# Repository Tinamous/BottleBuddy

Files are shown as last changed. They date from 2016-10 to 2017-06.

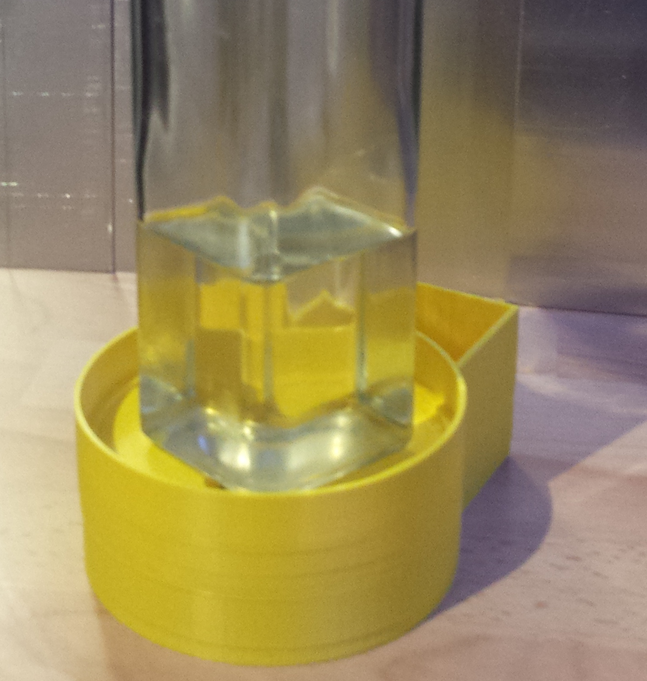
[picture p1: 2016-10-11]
Media/SmallOliveOil.png

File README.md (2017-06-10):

# BottleBuddy

Bottle Buddy is a Internet connected smart scale to monitor the amount of product in a bottle.

## Uses

* Stock control of bottled products
** Chemicals in a lab
** Reagents at a testing station
** Shampoo in a salon
** Domestic products (bleach, shampoo, etc) in the home.
** Liquors/spirits in a bar
* Monitoring chemicals in a lab to track usage (e.g. poisons usage)
* Refilling of reagents bottles
* Supply management to facilitate re-ordering as the bottle gets empty or used.
* Predictive ordering based on use
* Shelf life tracking from initial receipt and first use

### Example use case:

A river polution testing laboratory uses pH 4 and 7 buffer solutions to calibrate their pH Electrodes. 
Tests are run most days the electrodes are calibrated at least once, they use approximatly 25-75ml from each buffer solution.
The buffer solution which comes in 1L bottles with each bottle costs $70.
Once the buffer is opened it needs to be used within 28 days and has a shelf life of 1 year from the date of delivery.

Due to the cost and shelf life the lab only orders a new bottle of each buffer solution when they are getting low allowing for about a 3 day delivery time.

The lab is a remote testing station which is only occupied whilst the technician is there for a few hours running the tests, the technician is responsible 
for brining the required reagents with them as and when new stock is needed.

#### How Bottle Buddy helps

Delivery of new Reagents:

When new buffer solutions are brought a RFID sticked is placed on the bottom of the bottle to track it. The bottle is then placed on the Bottle Buddy where it
registers the RFID identifier and an initial weight, this is logged and as the RFID token is new the bottle assigned a delivery date to ensure that the 
shelf life restriction is monitored. 

By knowing the location of the Bottle Buddy the system also knows the location of this reagent, the technician can then use their phone or computer to 
assign additional details to the bottle as required and possibly print out a more human readable label to go with the bottle. This additional data may have been pre-programmed 
into the FRID tags (e.g. they may have tags specifically for the pH 7 buffer which include meta-data about shelf life, reagent name, etc.), or they may use a 
special identity tag after the reagent has been placed on Bottle Buddy to indicate it's type.

Day to day usage:

Once the technician has finished for the day they clean up and put away the equipment, part of this includes dropping each of the buffer
solution bottles onto Bottle Buddy, which then measures the weight of the bottle and records this. When the bottle weight drops below a 
pre-defined level, or the system determins the bottle will be empty within a certain timeframe an email is sent to the purchasing 
department or stores requesting a new bottle be delivered to the technician.

By tracking the weight of the bottle the tracking applicaiton can tell that the reagent is in use (i.e. the weight has decreased indicating it has
been opened and is in use), this allows the tracking of the shortened shelf life to ensure that a replacement is available before the 28 day usage is up.

Emails sent to the purchasing department can include details of when this reagent is required by, how much is typically used and who needs it, order codes and other information required for purchasing.

Other than the very brief initial RFID token assignment and the few seconds required to put the reagen on Bottle Buddy at the end of the day no time is 
lost with requesting replacement reagents, or discovering that the reagent has run out because the technician forgot to re-order any, good quality
reagent can be assured by the tracking of shelf life, and improved planning by usage monitoring can be achieved.

## Features: 

### V1.0

* Weight measurement with HX711 PCB and Load Cell
* Potential to drive NeoPixel ring (needs to be run from battery as 5V USB supply will cause problems).
* WiFi connectivity with Particle Photon
* Doesn't provide much in the way of power saving options, the Photon can be put to sleep and woken to check for an item on the scale. An accelerometer
can be added by connecting the wires to the appropriate I2C and power pins and glued to the PCB.
* Simple construction, can be hand soldered.

### V1.1

* Has an accelerometer (MMA8452Q)to detect a pulse when something is placed on the scale
* Photon can be kept in deep sleep and woken by the accelerometer to enable longer battery life.
* Power to the NFC PCB and optional NeoPixels can be controlled via p-Channel MOSFET switches.
* Charge monitoring for Li-Ion batteries with a Max1704x
* Simple temperature measurements with a DS18B20 (which could be glued to the load cell for better accuracy if needed)
* Temperature, humidity and pressure measurements with a BME280
* Swapped to headerless Photon to reduce depth of PCB on both sides
* Piezo buzzer to provide user feedback
* Single point LED at the front of the top to provide simple user feedback
* Needs reflow soldering / stencil for the BME280, Max1704x and MMA8452Q - these can all be left off through for more basic functionality

## Modes of operation

## 3D Printable

Boddle Buddy is made of two main shells, a top and a bottom. Both are designed so that the user facing part should have a nice smooth finish.

### Base - BottleBuddyBase.scad/.stl

This is the lower half of the assembly, it has holes for the the counter sunk M5x16 machine screws required by the load cell, [currently] a hole for 
the HX711 load cell amplifier PCB to be mounted (this is expected to be PCB mounted from V1.1 of the PCB), and a compartment for the battery to 
sit in.

It has 4 10mm recesses for feet to be placed in so that the floor isn't resting on a possibly uneven surface.

It may also have a hole to provide power in (depending on options

### Top - BottleBuddyTop.scad/.stl

This is the upper half, the PCB is mounted to the inside of this. This is connected to the lower half only by means of the load cell.

A skirt is printed aroud below the top half to prevent ingress of liquid into the lower half from above and to improve the look (rather than having a void). The skirt has a clearance around it to 

The load cell uses 2x M4x20 counter sunk machine screws from the top.

Inset in the top is a PN532 NFC reader (e.g. http://www.ebay.co.uk/itm/NXP-PN532-NFC-RFID-Module-V3-Kits-Reader-Writer-For-Arduino-Android-Phone-Module-/291939590305?hash=item43f8f4a0a1:g:p2kAAOSwnbZYJTmy)

This requires connecting up through the I2C connection with a 4 way header (solder into the NFC module first) through to the lower PCB, as well as 2 wires from the RSTO and IRQ pads connecting to the appropriate "test points" on the PCB.

The main PCB should be fitted inside with 2x self tappers through the holes either side of the load cell. 

The open hole for the LED on the V1.1 PCB (not present on the V1.0 PCB) should be covered with electrical tape to prevent resin coming through when poured onto the top.

When everything is mounted it can be tested to check for connection problems and then a layer of clear epoxy resin poured onto the top to the level of the raised lip (or just below to prevent overflow!)

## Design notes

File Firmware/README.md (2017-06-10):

# BottleBuddy Firmware

This folder contains the firmware required to run the BottleBuddy as a Reagent Tracker. 

This is based on the Particle Photon. It is assumed you are familiar with programming the Photon via the Particle Build system.

## Programming the Photon

To use the code open a new code application in the Particle Build environment (https://build.particle.io)

Unfortunatly at present Particle don't have a nice way to bundle applications for sharing using the build environment, you can use their console based compiler if you prefer, but this guide is for the web ide.

Create a new Application (<>).

Paste in the bottlebuddy-v1.0.ino code.

Add the following libraries using the Build library manager:

* Adafruit_PN532
* neopixel
* OneWire

Add new tabs using the (+) in the top right:

* HX711
* SparkFunMMQ8452Q

You should get a .cpp and .h tab for each of those. Paste in the appropriate files (note theirs a bit of a bug where pasting in the .cpp code will end up in the .h file as well).

The HX711 library is available through the Particle Library system as HX711ADC however I had some issues with it at the original time of writing so brought it into the project as a C++ file, also the tare function uses an incorrect type (double should be long). 

The MMQ8452Q library didn't support configuration of tap interrupt events so I've modified that slightly from the original SparkFun library to support Tap Interrupts.

You will find the build environment has duplicated the #include statements. Remove the duplicates.

Ensure that the pin definitions in the .ino file match your build, these have changed between V1.0 and V1.1 of the PCB.

Click the verify icon and the application should build.

Ensure you have the correct device selected and the firmware version is set to 6.2 then flash the photon code.

## Post Programming:

Once the Photon has flashed it is going to spend most of its time asleep so we won't be able to re-flash the device without doing something special. 

Their are a few ways to keep the Photon connected to allow firmware updates. The KeepAwake pin (A2) is probably the most useful, particularly on a prototype board set-up. V1.1 of the PCB has a test point that can be soldered too if required.

Alternatively we can place the Photon in Safe Mode. 

To place the photon in Safe Mode, hold both Set-Up and Reset buttons down, release Reset and wait for the LED to flash Purple (it does this almost immediately), then release the Set-Up button. The Photon will now connect to the Particle Cloud and we can updated it, but it won't run any of our code until it is reset (manual or due to firmware update).

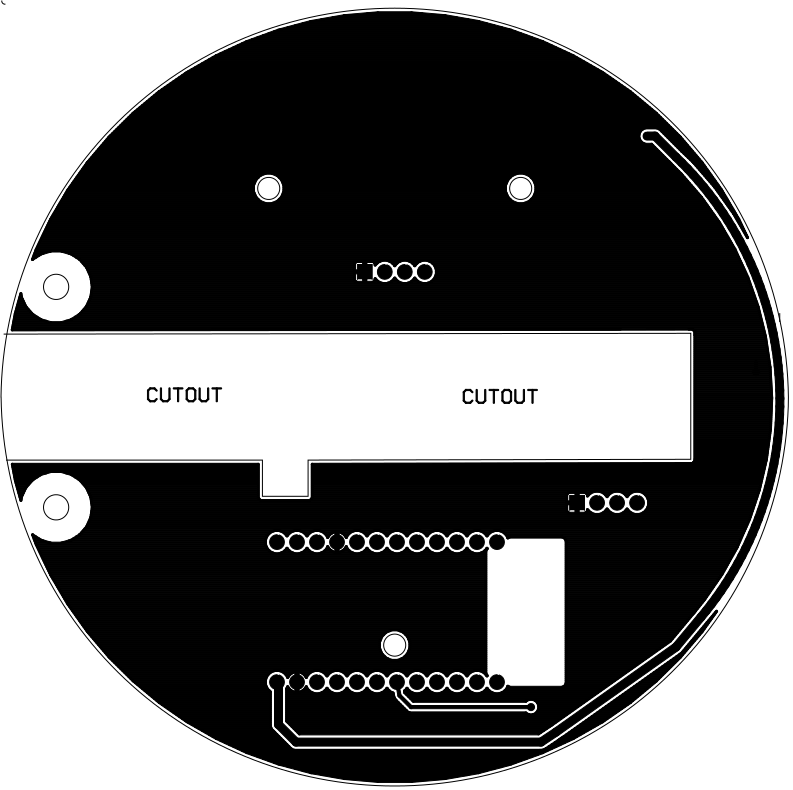
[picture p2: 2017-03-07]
Media/PCB/bottom_copper.png

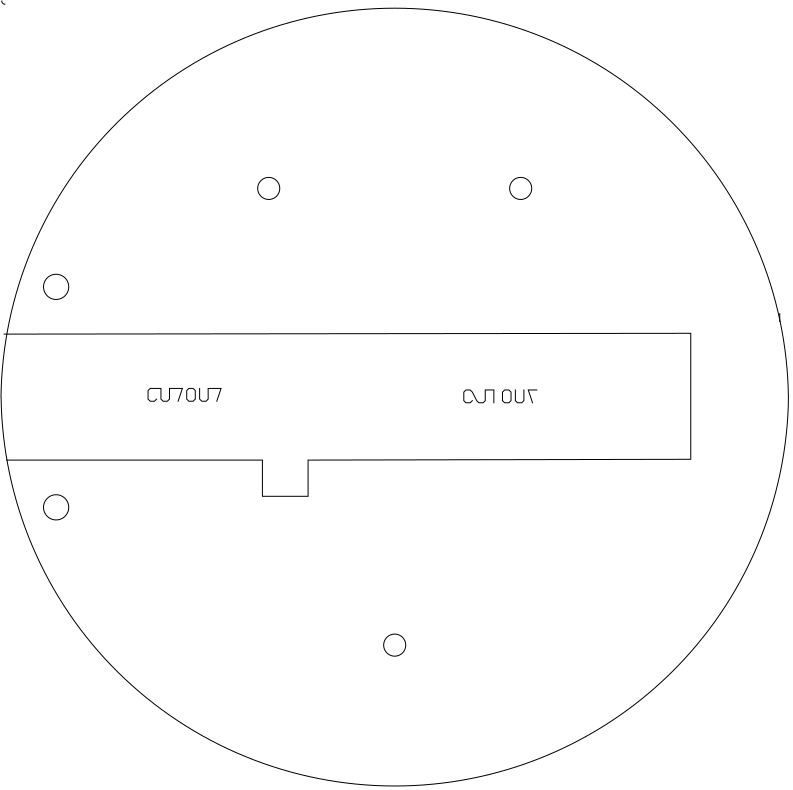
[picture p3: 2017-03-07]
Media/PCB/mill.png

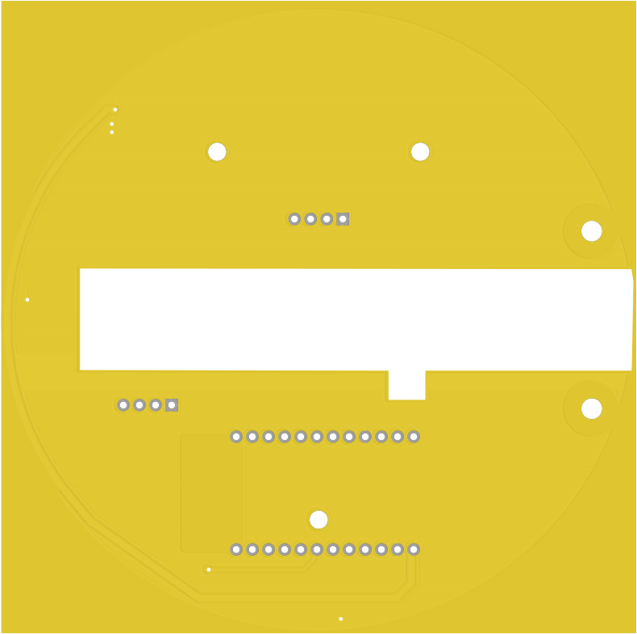
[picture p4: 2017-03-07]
Media/PCB/bottom.png

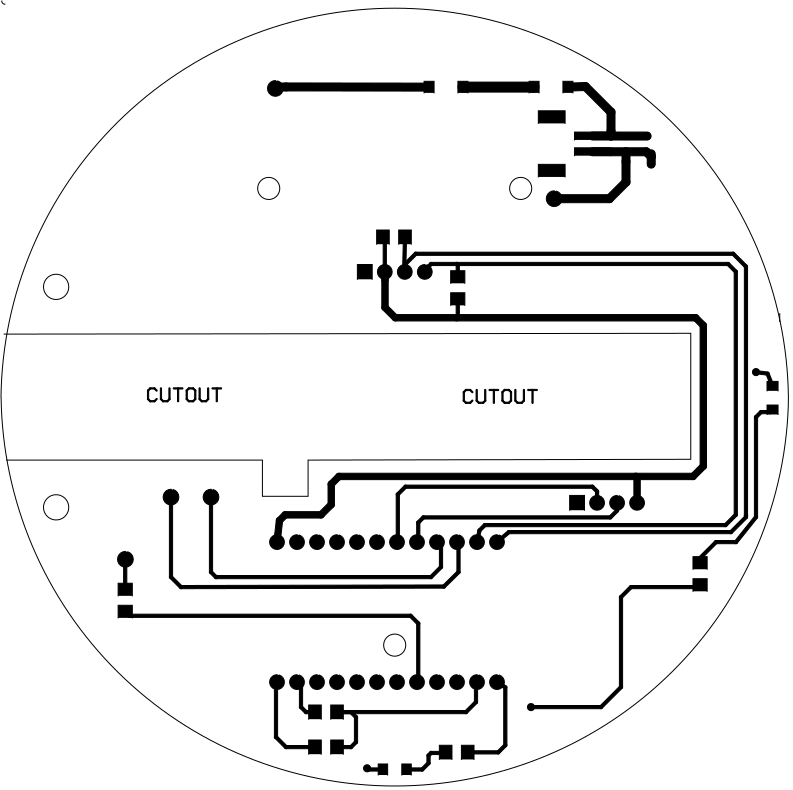
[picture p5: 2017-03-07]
Media/PCB/top_copper.png

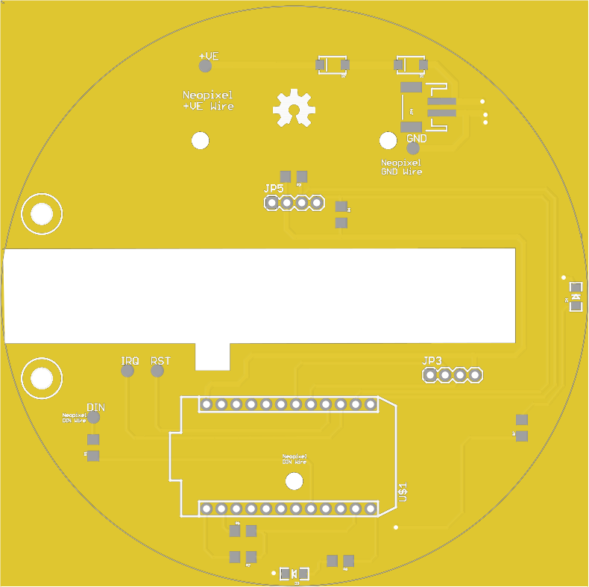
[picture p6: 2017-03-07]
Media/PCB/top.png

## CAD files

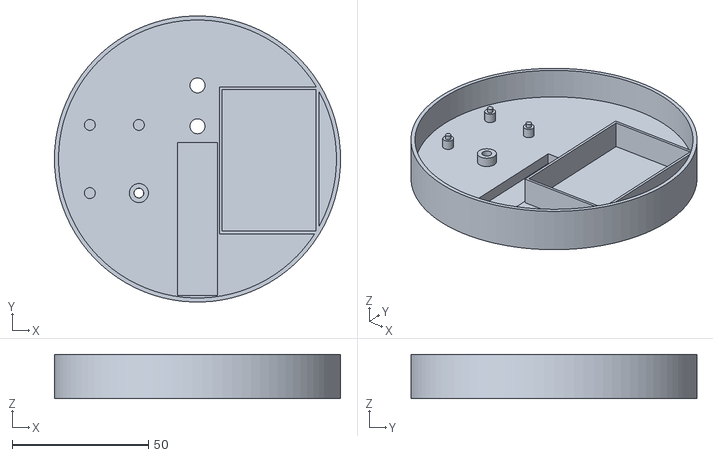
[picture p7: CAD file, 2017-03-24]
BottleBuddyBase.stl
105.0 x 104.9 x 16.2

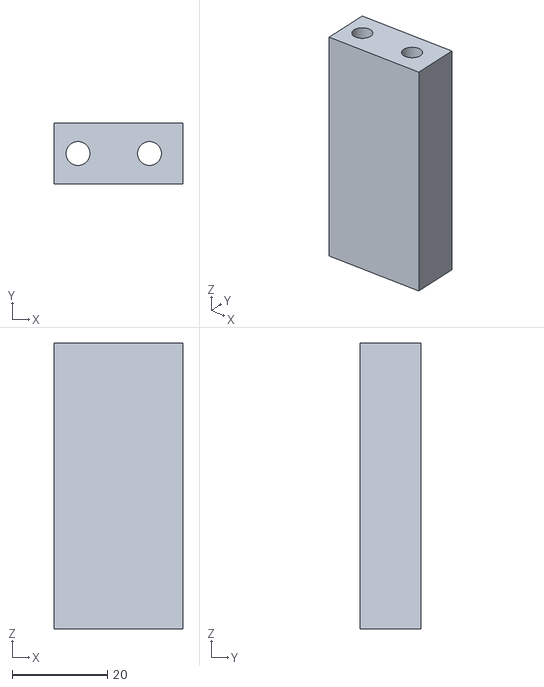
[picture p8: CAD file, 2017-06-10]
Case/ExtraBits/LoadCellSpacer-60mm.stl
27.0 x 12.8 x 60.0

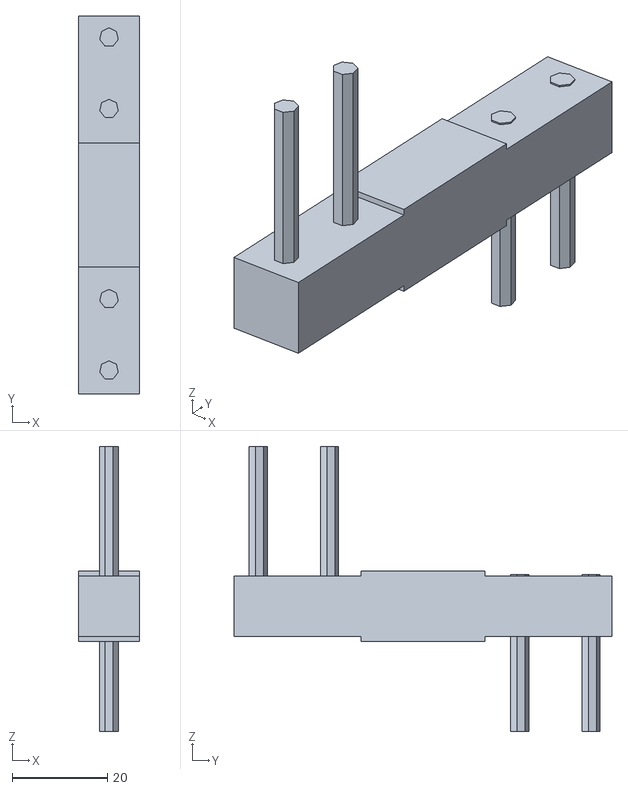
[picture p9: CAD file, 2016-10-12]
Case/LoadCellModel.stl
12.8 x 79.5 x 60.0

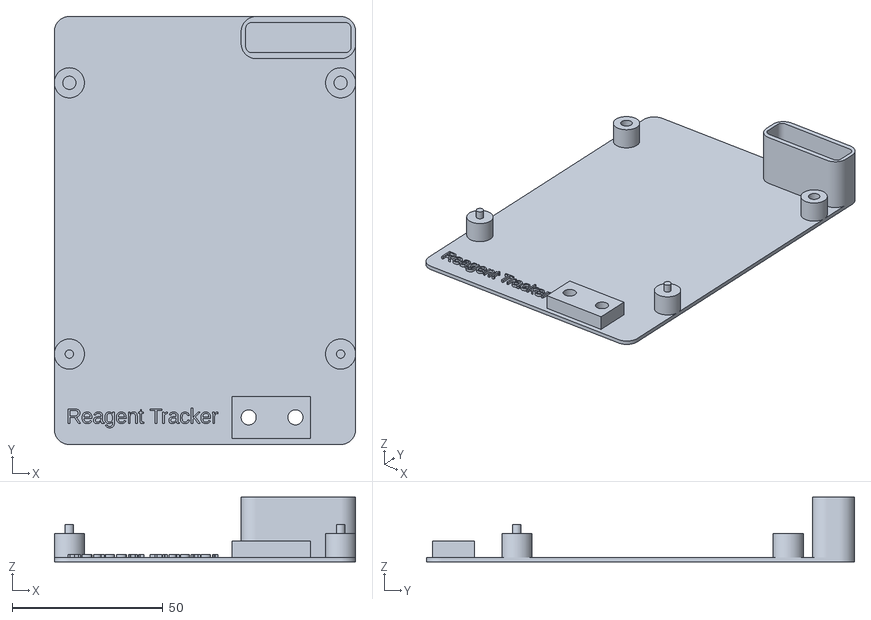
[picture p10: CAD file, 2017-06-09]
Case/Prototype/PrototypeBaseWithLoadCell.stl
100.0 x 142.0 x 21.5

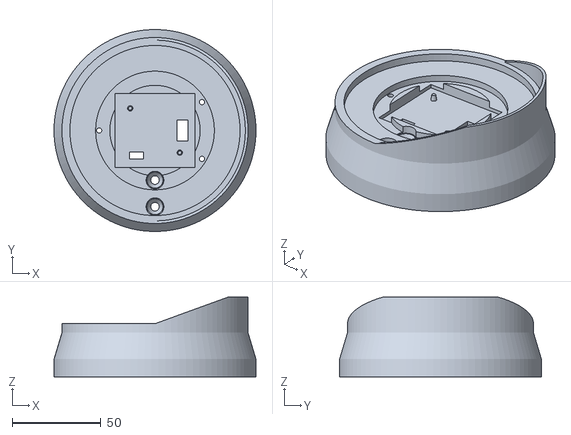
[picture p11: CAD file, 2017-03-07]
BottleBuddyTop.stl
114.0 x 113.9 x 45.0

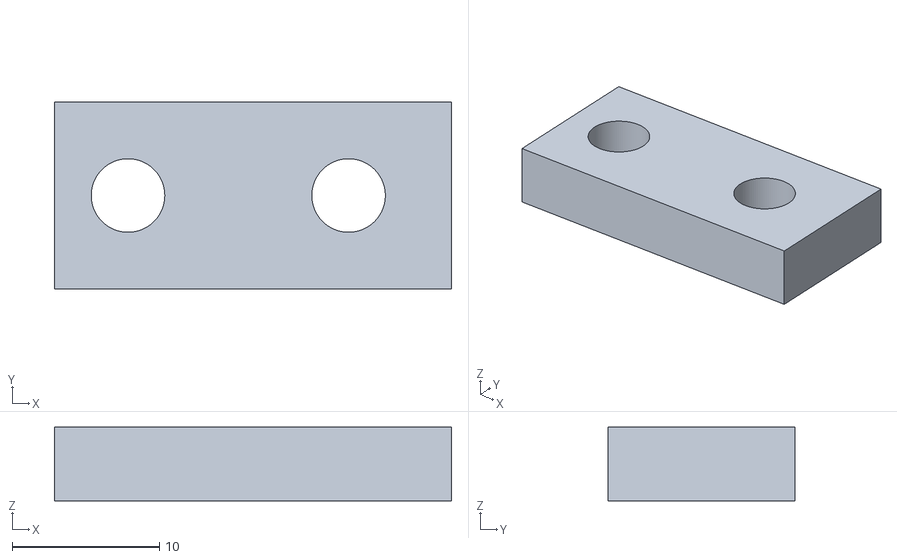
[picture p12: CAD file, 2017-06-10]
Case/ExtraBits/LoadCellSpacer-5mm.stl
27.0 x 12.8 x 5.00

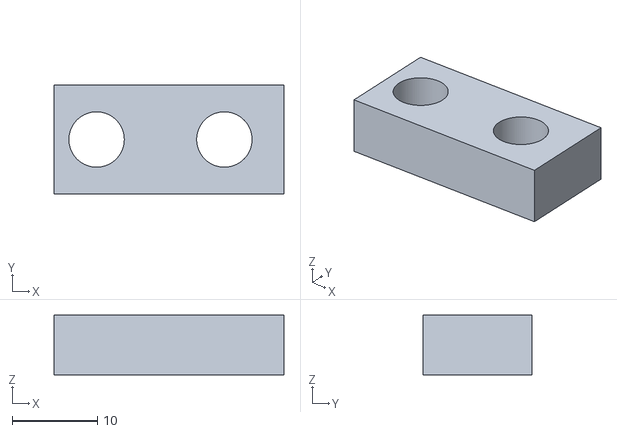
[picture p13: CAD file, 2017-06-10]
Case/ExtraBits/LoadCellSpacer-7mm.stl
27.0 x 12.8 x 7.00

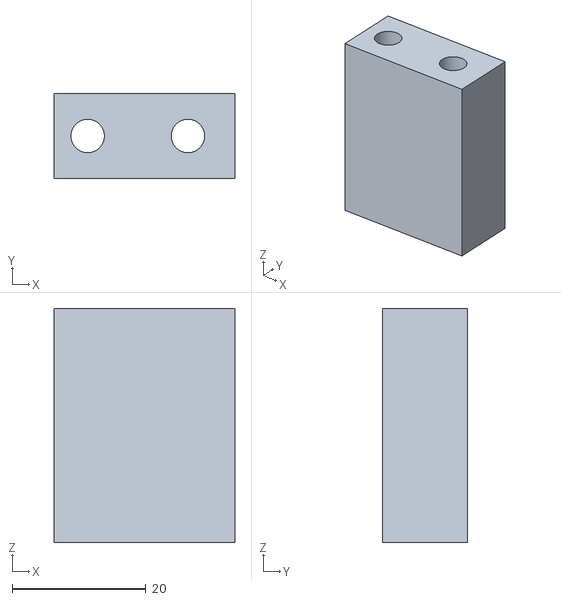
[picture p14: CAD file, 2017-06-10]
Case/ExtraBits/LoadCellSpacer-35mm.stl
27.0 x 12.8 x 35.0

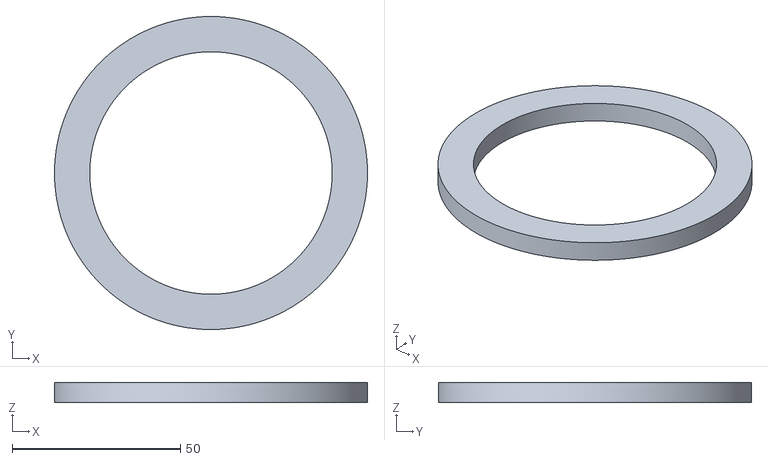
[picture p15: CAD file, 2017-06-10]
Case/ExtraBits/TopSpacer.stl
93.0 x 93.0 x 6.00

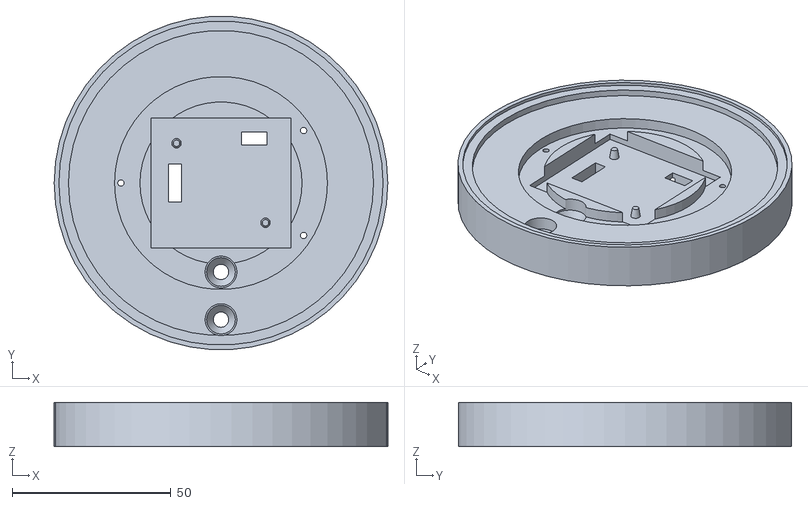
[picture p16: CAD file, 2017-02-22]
Case/ExtraBits/NfcAndNeoPixelCutouts.stl
105.0 x 104.8 x 14.0

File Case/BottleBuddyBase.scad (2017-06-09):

$fn = 360;
bottleDiameter = 100;
wallThickness = 3;
bottlePadding = 2;
baseFloorThickness = 2;

loadcellHeight = 12.75;
loadcellWidth = 12.75;
loadcellLength = 79.5;
loadCellOffset = -48;

gabBetweenTopAndBottom = 1.5;
wallHeight=baseFloorThickness + loadcellHeight - gabBetweenTopAndBottom;

// Dont need such a large height as the top covers most of it.
wallHeight = 5;
echo ("WallHeight (i.e. total height)=" ,wallHeight);

loadCellPcbXOffset = -36;
loadCellPcbYOffset = -32;
loadCellPcbWidth = 21;
loadCellPcbSpaceBetweenHoles = 18;

// ====================================================
// Models
// ====================================================
module showBottleHolder() {
    import("BottleBuddyTop.stl");
}

module QIReceiver() {
    color("Black", 50) {
        cube([45, 75,1]);
    }
}

module loadCellPcb() {
    cube([23, 33, 6]);
    
    translate([2.5,2.5, -3]) {
        cylinder(d=2, h=20);
        
        translate([0,25, 0]) {
            cylinder(d=2, h=20);
        }
    }
    
    // 15mm gap between screws
    
    translate([2.5 + loadCellPcbSpaceBetweenHoles,2.5, -3]) {
        cylinder(d=2, h=20);
        
        translate([0,25, 0]) {
            cylinder(d=2, h=20);
        }
    }
}

module importLoadCellModel() {
    import("LoadCellModel.stl");
}

// Load cell model to project into the design for fit.
module loadCell() {
    //import("LoadCellModel.stl");
    
    //translate([-30,-(loadcellWidth/2),-2]) {
    rotate([0,0,90]) {
        translate([loadCellOffset, -(loadcellWidth)/2 ,-0.1]) {
        
        //color("Gainsboro", 50) { 
            difference() {
                union() {
                    cube([loadcellLength, loadcellWidth, loadcellHeight]);
                    // strain gauge placement + goo
                    translate([(loadcellLength-26)/2,0,loadcellHeight]) {
                        cube([26,loadcellWidth,1]);
                    }
                    translate([(loadcellLength-26)/2,0,-1]) {
                        cube([26,loadcellWidth,1]);
                    }
                }
                union() {
                    translate([5.0, (12.75/2),0]) {
                        // Bigger top connector holes
                        // to help align with top when visual testing
                        #cylinder(d=4, h=40);
                    }
                    translate([20, (12.75/2),0]) {
                        #cylinder(d=4, h=40);
                    }
                    //60
                    translate([60, (12.75/2),0]) {
                        cylinder(d=4, h=13);
                    }
                    translate([75, (12.75/2),0]) {
                        cylinder(d=4, h=13);
                    }
                }
          //  }
        }
    }
    }
}

// ====================================================

// ====================================================
// Load cell placement
// ====================================================
// Holes for the Load Cell
module loadCellHoles() {
    //translate([-30,-(loadcellWidth/2)-1,-0.1]) {
    rotate([0,0,90]) {
        translate([loadCellOffset,-(loadcellWidth+2)/2, -0.1]) {
            // Load cell is raised slighly now so no need for a cut out.
            // allow more cutout space for the load cell to hover over
            //translate([-2,0, 1]) {
            //    #cube([56,loadcellWidth+2,baseFloorThickness]);
            //}
            
            //  bolt holes
            translate([00,(12.75/2)+1,0]) {
                translate([60,0,0]) {
                    loadCellHole();
                }
                translate([75, 0,0]) {
                    loadCellHole();
                }        
            }
           
        }
    }
}

module loadCellHole() {
    // M5 thread in load cell
    // Small recess for the bolt head
    // so we don't end up with any metal on a surface if
    // no feet are fitted.
    translate([0,0,-0.1]) {
        cylinder(d=10, h=1.21);
    }
    // Counter sink
    translate([0,0,1.1]) {
        cylinder(d1=10, d2=5.5,h=3.5);
    }
    // hole for threaded bolt part
    translate([0,0,3]) {
        cylinder(d=5.5, h=10);
    }
}

// A guard around the load cell to allow pouring of 
// potting compound around the electronics without getting into the load cell.
module loadCellGuard() {
    rotate([0,0,90]) {
        translate([loadCellOffset-3,-(loadcellWidth)/2 - 4, baseFloorThickness]) {
            
            difference() {
                union() {
                    cube([loadcellLength+8,loadcellWidth+8,wallHeight-baseFloorThickness]);
                }
                union() {
                    translate([1,+2, 0]) {
                        cube([loadcellLength + 4,loadcellWidth+4,loadcellHeight]);
                    }
                    // cut out wire exit
                    translate([loadcellLength + 4,2, loadcellHeight-4]) {
                        cube([6,4,4]);
                    }
                }
            }
            
        }
    }
}

// Guard modified to help keep wires out but skipping the battery box.
module loadCellGuard2() {
    rotate([0,0,90]) {
        translate([loadCellOffset-3,-(loadcellWidth)/2 - 4, baseFloorThickness]) {
            
            difference() {
                union() {
                    cube([loadcellLength+8,loadcellWidth+4,wallHeight-baseFloorThickness]);
                }
                union() {
                    translate([1,+2, 0]) {
                        cube([loadcellLength + 4,loadcellWidth+2,loadcellHeight]);
                    }
                    // cut out wire exit
                    translate([loadcellLength + 4,2, loadcellHeight-4]) {
                        cube([6,4,4]);
                    }
                }
            }
            
        }
    }
}


module loadCellPadding() {
    
        rotate([0,0,90]) {
            translate([loadCellOffset,-(loadcellWidth+2)/2,-0.1]) {
            // allow more cutout space for the load cell to hover over
                translate([56,0,baseFloorThickness]) {
                   //cube([26,loadcellWidth,loadCellZPadding]);
                }
        }
    }
}

// ====================================================
// Load cell PCB support pins/pads/holes
// ====================================================

// Bolt hole for load cell PCB.
module pcbSupport(d, h) {
    difference() {
        union() {
            cylinder(d=7, h=h);
        }
        union() {
            translate([0,0,-0.1]) {
                cylinder(d=d, h=h+2);
            }
        }
    }
}

// Pin for load cell PCB
module pcbPin(height) {
    cylinder(d=4, h=height);
    cylinder(d=2, h=height + 1.5);
}

// Mounting points in the base
// for the load cell amplifier PCB.
// This will eventually not be needed as the load
// cell PCB will move to the top PCB.
module loadCellPcbMount() {
pcbHeightOffset = 2.5;
    
    rotate([0,0,180]) {
        // Front supports (for load cell amplifier)
        translate([loadCellPcbXOffset,loadCellPcbYOffset,0]) {
            
            // Offset from top right corder for 
            // the pcb hole.
            translate([+2.5,+2.5, 1]) {
                pcbPin(pcbHeightOffset );
            }
            
            // left hand corner, use a screw to hold the PCB in place.
            translate([+2.5 + loadCellPcbSpaceBetweenHoles, +2.5, baseFloorThickness]) {
                // Hole for a M3 bolt to come through
                pcbSupport(3.6, 3.5 - baseFloorThickness);
            }
        
        
            translate([0,25,0]) {
                
                // Offset from top right corder for 
                // the pcb hole.
                translate([+2.5,+2.5,1]) {
                    pcbPin(pcbHeightOffset );
                    
                }
                
                // left hand corner
                translate([+2.5 + loadCellPcbSpaceBetweenHoles, +2.5, 1]) {
                    pcbPin(pcbHeightOffset );
                }
            }
        }
    }
}

module pcbSupports() {
    loadCellPcbMount();    
}

module pcbSupportHoles() {
   rotate([0,0,180]) {
        // Front supports (for load cell amplifier)
        translate([loadCellPcbXOffset,loadCellPcbYOffset,-0.1]) {
            translate([+2.5 + loadCellPcbSpaceBetweenHoles, +2.5, 0]) {
                cylinder(d1=7,d2=3.5, h=2);
                cylinder(d=3.5, h=18);
                
            }
        }
    }
}

// ******************************************************
// Battery/Power
// ******************************************************

module hollowFloorForBattery() {
    // Hollow out a little of the follow so the battery (or rather
    // the QI adaptor is closer to the base) default floor thickness
    // is 2mm, QI works at 3mm, not much tollerence left.
    cube([34, 52, 1]);
}
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

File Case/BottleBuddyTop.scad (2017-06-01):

$fn=360;

// Size of the bottle.
// 100mm Minimum to fit the PCB and allow space for the load cell
bottleDiameter = 100;
wallThickness = 3;
bottlePadding = 2;

// Overall height. If using "sliceTop" to slice the top lowering
// this will reduce the height to the flat part.
// otherwise this govenrs the overall outer wall
// height for the bottle to drop into.
height = 30;

loadcellHeight = 12.75;
loadcellWidth = 12.75;
loadcellLength = 80;
loadCellOffset = -48;

baseHeight = 2 + 9; // 2mm for loadcell scren + 12 mm for. (PCB?)

neoPixelPcbDepth = 3.4;
pcbDepth = neoPixelPcbDepth + 2;

// Size of the NFC PCB in the top of the unit
nfcPcbLength = 43;
nfcPcbWidth = 40;

// The area that gets cutout for the NFC PCB
paddedNfcPcbLength = nfcPcbLength+4; // 43
paddedNfcPcbWidth = nfcPcbWidth+5; // 40  

// Causes a diagonal cut through the top.
// If not set uses just a cylinder as the bottle holder.
sliceTop = true;

// We cover the NFC PCB and area
// with Epoxy to provide a water resitant
// seal for the NFC and inner electronics.
// How deep should this be.. (mm).
// Essentially governs the depth of the out rim of the 
// unit.
epoxyDepth = 4;

// NeoPixels.
includeNeoPixels = false;

// 0 : No skirt
// 2 : Version 2 Skirt
// 3 : Version 3 skirt
skirtOption = 2;

// PCB Pad height
// Gap between the base and the PCB.
// remember photon lets sticking through
// The lower the better to allow more room
// for the battery etc.
padHeight = 2;

// How much to reduce the PCB pad
// that the LED goes through.
// V1 PCB - reduce down by 2mm or so (padHeight) to allow for a regular
// 3mm LED to be inserted
// V1.1 PCB set to 0
ledPadAdjust = 3;

// ==============================================================
// Models to help visualise
// ==============================================================

module showModels() {
        
    //%loadCell();
    translate([0,0,-12.75]) {
        %importLoadCellModel();
    }
    
    
    translate([0,0,baseHeight - pcbDepth]) {
        rotate([0,0,180]) {
            % nfcPcb();
        }
    }
    
    if (includeNeoPixels) {
        translate([0,0,baseHeight - neoPixelPcbDepth]) {
            % neoPixelCirclePcb();
        }
    }
    
    // 3mm up due to PCB + 2mm layer
    translate([0,0,loadcellHeight + 5 + 5]) {
      //%bottle();
    }
}

module bottle() {
    cylinder(d=bottleDiameter, h=225);
}

module neoPixelCirclePcb() {
    
    difference() {
        union() {
            cylinder(d=66, h=3.4);
        }
        union() {    
            translate([0,0,-0.01]) {
                cylinder(d=52, h=3.42);
            }
        }
    }
}

module nfcPcb() {
nfcPcbHeight = 5;
    translate([-(43/2),-(40/2),16]) {
        
        difference() {
            union() {
                cube([43, 40,1.6]);
                // Dip switch. the tallest thing.
                translate([8.6,8.6,1.6]) {
                    cube([6,4,3]);
                }
                
                // I2C Connection
                translate([5,20-6,-18]) {
                    cube([4,12,18]);
                }
                
                // IRQ and Reset pins
                translate([29,32,-18]) {
                    cube([7,4,18]);
                }
                
                // The other Reset pin.... 
                translate([27,8,-18]) {
                    cube([5,4,18]);
                }
            }
            union() {
                // Mounting holes.                
                translate([43-7.5, 7.5,0]) {
                    #cylinder(d=3, h=nfcPcbHeight+0.01);
                }
                
                translate([7.5, 40-7.5,0]) {
                    #cylinder(d=3, h=nfcPcbHeight+0.01);
                }
            }
        }
    }
}

module importLoadCellModel() {
    import("LoadCellModel.stl");
}

module loadCell() {
    
    rotate([0,0,90]) {
        translate([loadCellOffset, -(loadcellWidth)/2 ,-0.1]) {
        
            difference() {
                union() {
                    cube([loadcellLength, loadcellWidth, loadcellHeight]);
                    // strain gauge placement + goo
                    translate([(loadcellLength-26)/2,0,loadcellHeight]) {
                        cube([26,loadcellWidth,1]);
                    }
                    translate([(loadcellLength-26)/2,0,-1]) {
                        cube([26,loadcellWidth,1]);
                    }
                }
                union() {
                    translate([5.0, (12.75/2),0]) {
                        // Bigger top connector holes
                        // to help align with top when visual testing
                        #cylinder(d=4, h=40);
                    }
                    translate([20, (12.75/2),0]) {
                        #cylinder(d=4, h=40);
                    }
                    //60
                    translate([60, (12.75/2),0]) {
                        cylinder(d=4, h=13);
                    }
                    translate([75, (12.75/2),0]) {
                        cylinder(d=4, h=13);
                    }
                }
            }
        }
    }
}

// ==============================================================

module loadCellHoles() {
    
    loadcellHeightOffset = 2;
    
    //translate([-30,-(loadcellWidth/2)-1,-2]) {
    translate([+(loadcellWidth/2),loadCellOffset,0]) {
            rotate([0,0,90]) {
            // Load Cell cutout to allow for movement.
            // Cut out extra to allow for top 
            // surface of the load cell.
            translate([26,-1, 0]) {
                cube([loadcellLength - 20, loadcellWidth+4, loadcellHeightOffset+2]);
            }
            
            //  bolt holes
            // Outside
            // Raise the bolt up x mm's so it has more material underneath
            translate([5.0, (12.75/2), 0]) {
                translate([0, 0, -10]) {
                    cylinder(d=4.8, h=11);
                }
            
                cylinder(d=4.8, h=7);
                
                // Countersink
                translate([0,0,5]) {
                    cylinder(d1=4.8, d2=9, h=4);
                }
                
                // Hollow out the remaining hole
                translate([0,0,8]) {
                    cylinder(d=10, h=9);
                }
            }

            // Inside
            translate([20.0, (12.75/2), 0]) {
                translate([0, 0, -10]) {
                    cylinder(d=4.8, h=11);
                }
                cylinder(d=4.8, h=7);
                
                // Countersink
                translate([0,0,5]) {
                    cylinder(d1=4.8, d2=9, h=4);
                }
                
                // Hollow out the remaining hole
                translate([0,0,8]) {
                    cylinder(d=10, h=9);
                }
            }
        }
    }
}

// Cutout in the top for the NFC pcb to rest in.
// and for holes to the lower PCB
module nfcPcbCutout() {

    
    // PCB
    // Make the PCB slot 
    translate([-paddedNfcPcbLength/2,-paddedNfcPcbWidth/2, baseHeight - pcbDepth + 0.1]) {
        cube([paddedNfcPcbLength, paddedNfcPcbWidth, pcbDepth]);
    }
    
    // PCB Cables, through to the bottom compartment
    translate([-nfcPcbLength/2,-nfcPcbWidth/2, baseHeight - pcbDepth + 0.1]) {    
        // I2C Connection
        translate([3,(nfcPcbWidth/2)-6,-8.1]) {
            cube([5,12,8.2]);
        }
        
        // IRQ and Reset pins
        translate([29,32,-8.1]) {
            cube([7,4,8.2]);
        }
        
        // The other Reset pin.... 
        translate([27,8,-8.1]) {
            cube([5,4,8.2]);
        }
    }
        
    translate([28,0,0]) {
        translate([-1,-13,0]) {
            //cube([3, 26, 8]);
        }
        translate([0,9-5,0]) {
            //#cube([2, 5, 8]);
        }
    }
}

// PCB goes directly on the base
// These are wrong at present, PCB holes have changed for Neopixels so these need to be updated.
module nfcPcbPins() {
nfcPcbHeight = 2;
    translate([-(nfcPcbLength/2),-(nfcPcbWidth/2), baseHeight - pcbDepth]) {
        // Mounting pins.                
        translate([nfcPcbLength-7.5, 7.5,0]) {
            cylinder(d1=3,d2=2, h=nfcPcbHeight+0.01);
        }
        
        translate([7.5, nfcPcbWidth-7.5,0]) {
            cylinder(d1=3,d2=2, h=nfcPcbHeight+0.01);
        }
    }
}
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

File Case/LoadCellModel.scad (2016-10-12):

loadcellHeight = 12.75;
loadcellWidth = 12.75;
loadcellLength = 79.5;
loadCellOffset = -48;

module loadCell() {
    
    rotate([0,0,90]) {
        translate([loadCellOffset, -(loadcellWidth)/2 ,-0.1]) {
            
            difference() {
                union() {
                    cube([loadcellLength, loadcellWidth, loadcellHeight]);
                    
                    // strain gauge placement + goo
                    translate([(loadcellLength-26)/2,0,loadcellHeight]) {
                        cube([26,loadcellWidth,1]);
                    }
                    translate([(loadcellLength-26)/2,0,-1]) {
                        cube([26,loadcellWidth,1]);
                    }
                    
                    // Project bolts up
                    translate([5.0, (12.75/2),0]) {
                        // Bigger top connector holes
                        // to help align with top when visual testing
                        cylinder(d=4, h=40);
                    }
                    translate([20, (12.75/2),0]) {
                        cylinder(d=4, h=40);
                    }
                    
                    // Project bolts down
                    translate([60, (12.75/2),-20]) {
                        cylinder(d=4, h=33);
                    }
                    translate([75, (12.75/2),-20]) {
                        cylinder(d=4, h=33);
                    }
                }
                union() {
                    translate([5.0, (12.75/2),0]) {
                        // Bigger top connector holes
                        // to help align with top when visual testing
                        //#cylinder(d=4, h=40);
                    }
                    translate([20, (12.75/2),0]) {
                        //#cylinder(d=4, h=40);
                    }
                    //60
                    translate([60, (12.75/2),0]) {
                        //cylinder(d=4, h=13);
                    }
                    translate([75, (12.75/2),0]) {
                        //cylinder(d=4, h=13);
                    }
                }
          //  }
        }
    }
    }
}

loadCell();

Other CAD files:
Case/ExtraBits/LoadCellSpacer.stl
Case/ExtraBits/LoadCellSpacer.scad
Case/ExtraBits/NfcAndNeoPixelCutouts.scad
Case/ExtraBits/TopSpacer.scad
Case/Prototype/PrototypeBaseWithLoadCell.scad

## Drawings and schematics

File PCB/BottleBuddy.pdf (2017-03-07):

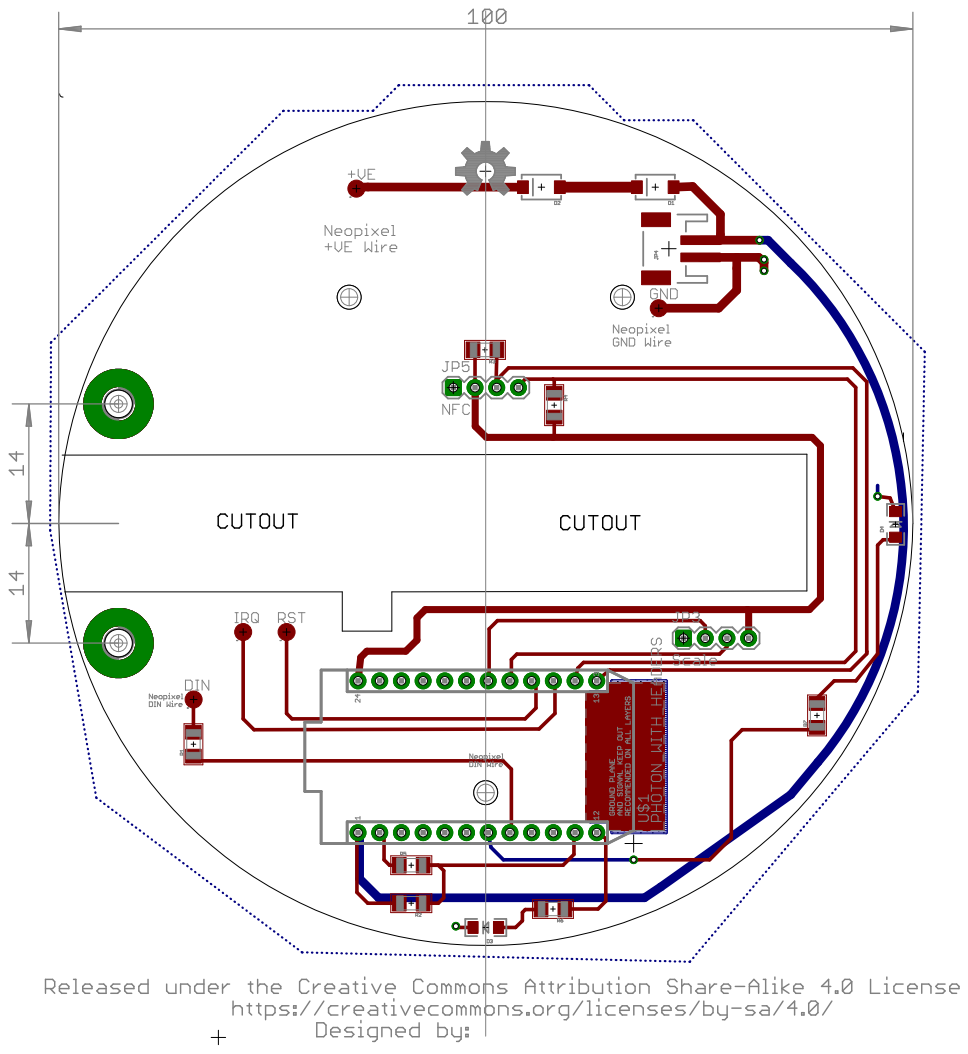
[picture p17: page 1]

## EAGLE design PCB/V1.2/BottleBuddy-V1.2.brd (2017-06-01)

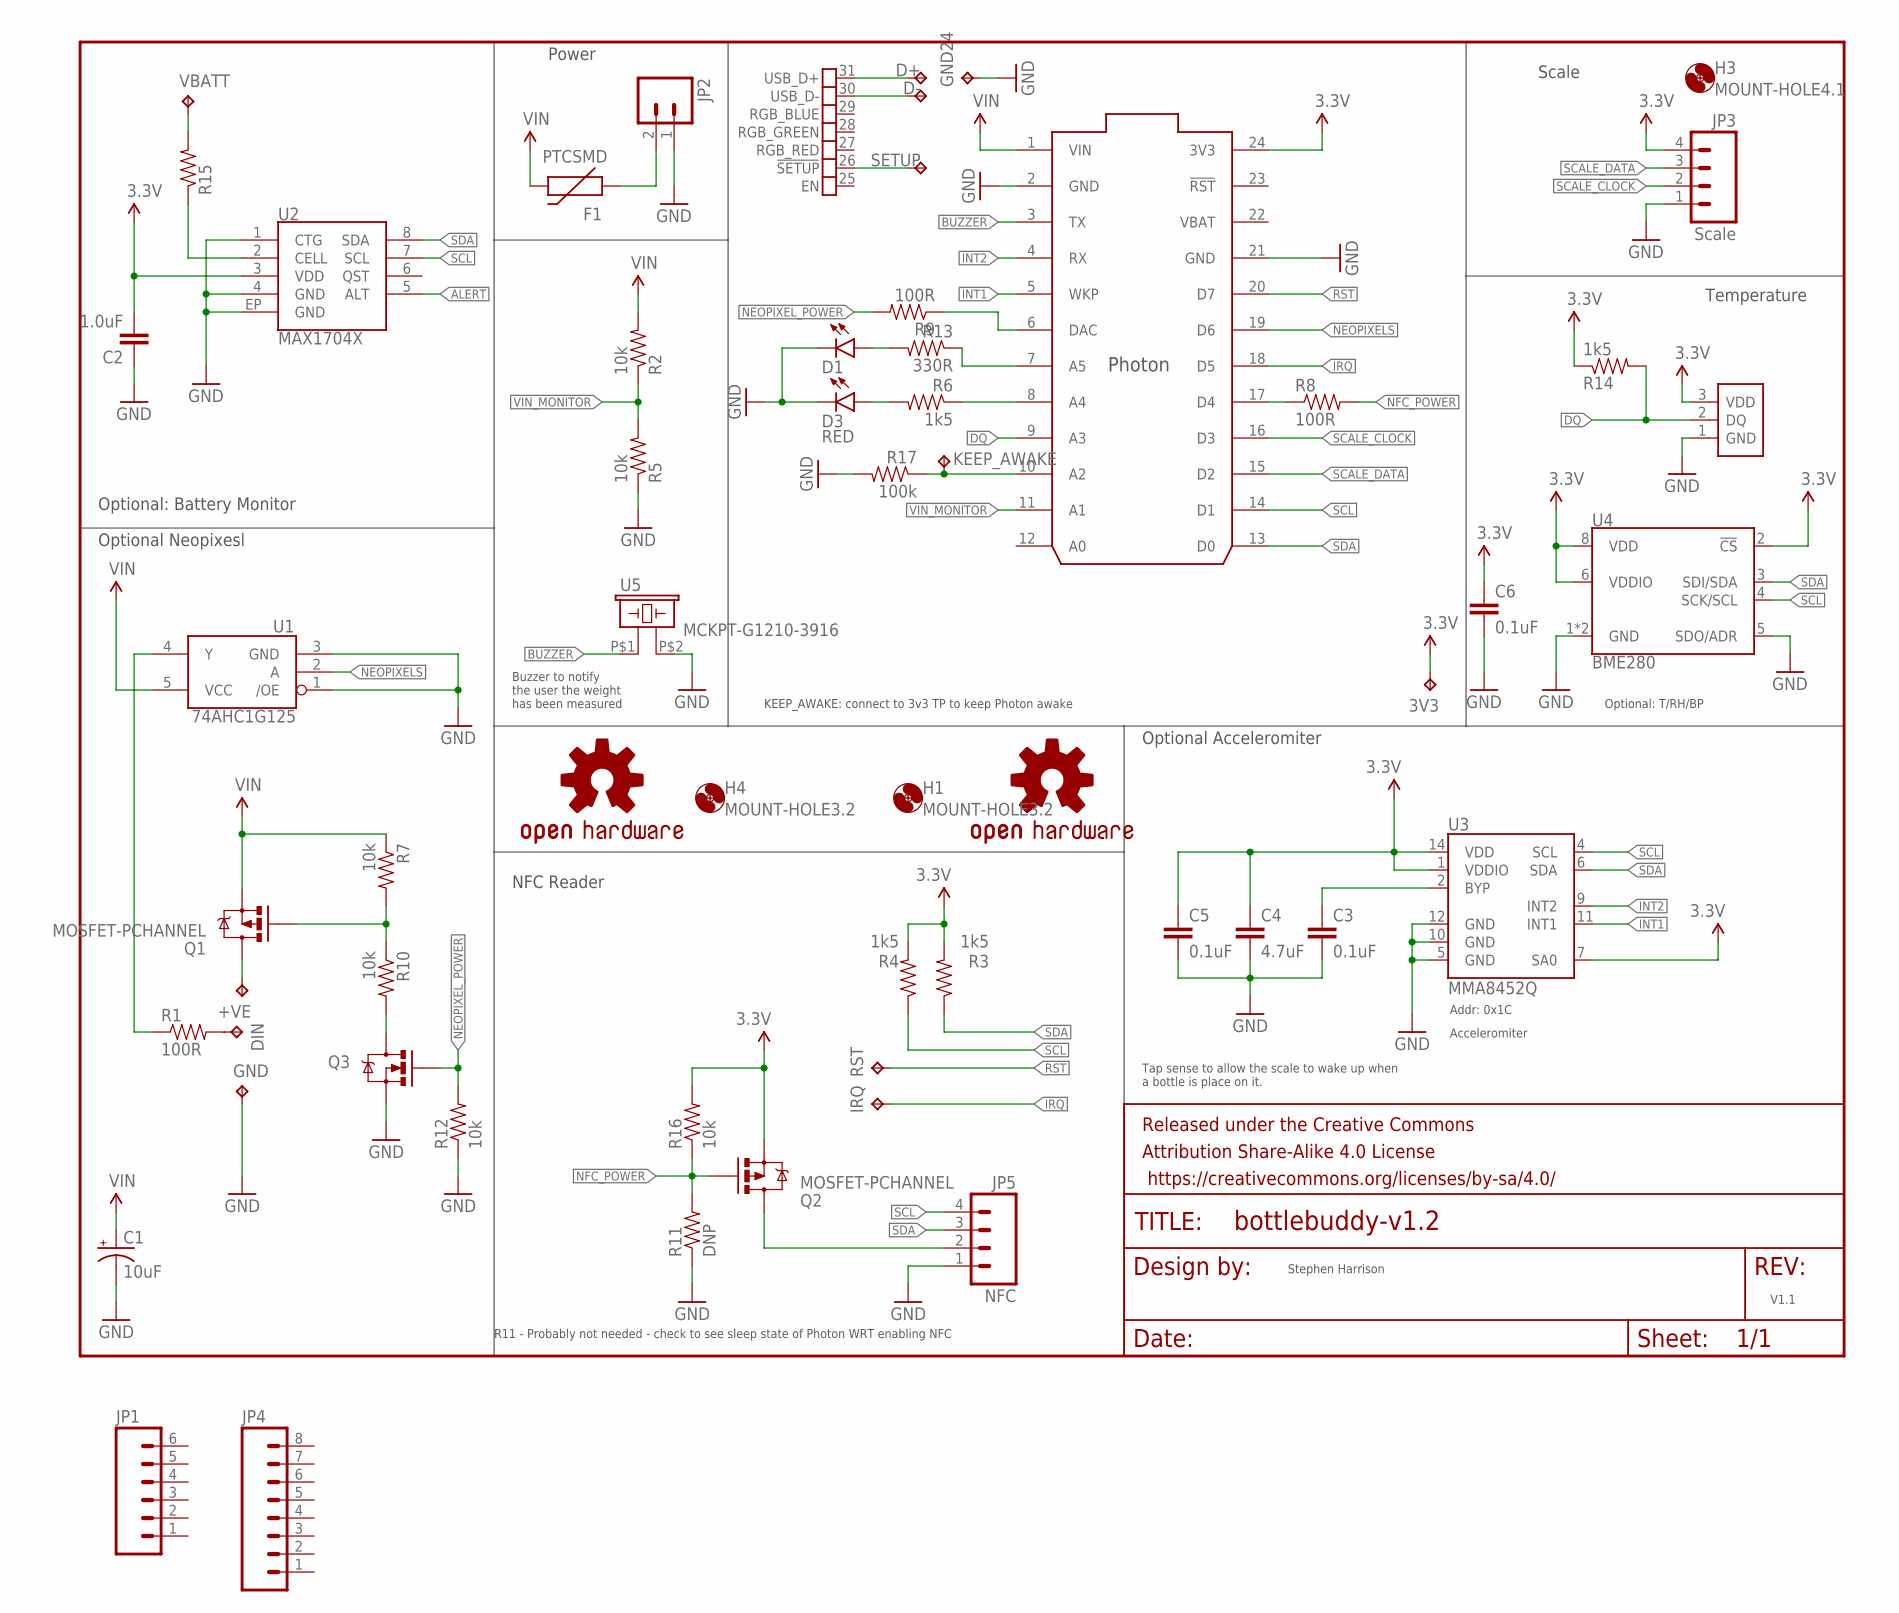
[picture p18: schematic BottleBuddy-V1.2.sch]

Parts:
3V3: TPTP20R; TP20R
+VE: TPTP20R; TP20R
C1: 10uF; EIA3216
C2: 1.0uF; 0805-CAP
C3, C5, C6: 0.1uF; 0805
C4: 4.7uF; 0805
D1: LED1206-BOTTOM; LED-1206-BOTTOM
D3: RED; LED-1206
D+: TPTP20R; TP20R
D-: TPTP20R; TP20R
DIN: TPTP20R; TP20R
F1: PTCSMD; PTC-1206
FRAME1: FRAME-LETTER; CREATIVE_COMMONS
GND, GND24: TPTP20R; TP20R
H1, H4: MOUNT-HOLE3.2; 3,2
H3: MOUNT-HOLE4.1; 4,1
IRQ: NFC IRQ; TP20R
JP1: M06SILK_FEMALE_PTH; 1X06
JP2: M02-JST-2MM-SMT; JST-2-SMD
JP3: Scale; 1X04
JP4: M08SILK_FEMALE_PTH; 1X08
JP5: NFC; 1X04
KEEP_AWAKE: TPTP20R; TP20R
LOGO1, LOGO2: OSHW-LOGOL; OSHW-LOGO-L
Q1, Q2: MOSFET-PCHANNEL; SOT23-3
Q3: 200mA/50V; SOT23-3
R1, R8, R9: 100R; 1206
R2, R5, R7, R10, R12, R16: 10k; 1206
R3, R4, R6, R14: 1k5; 1206
R11: DNP; 1206
R13: 330R; 1206
R15: RESISTOR1206; 1206
R17: 100k; 1206
RST: TPTP20R; TP20R
S1: SENSOR-DS18B20; TO-92-TRIANGLE
SETUP: TPTP20R; TP20R
U1: 74AHC1G125; SOT23-5
U2: MAX1704X; TDFN-8
U3: MMA8452Q; QFN-16_0.5MM
U4: BME280; LGA-8-2.5X2.5
U5: MCKPT-G1210-3916; BUZZER-12MM
U$1: PHOTON_SMD
VBATT: TPTP20R; TP20R

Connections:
3.3V: 3V3.TP, C2.2, C4.1, C5.1, C6.1, JP3.4, Q2.2 (S), R3.2, R4.2, R14.1, R16.2, S1.3 (VDD), U2.3 (VDD), U3.1 (VDDIO), U3.7 (SA0), U3.14 (VDD), U4.2 (!CS), U4.6 (VDDIO), U4.8 (VDD), U$1.24 (3V3)
ALERT: U2.5 (ALT)
BUZZER: U5.P$1 (1), U$1.3 (TX)
DQ: R14.2, S1.2 (DQ), U$1.9 (A3)
GND: C1.C (-), C2.1, C3.2, C4.2, C5.2, C6.2, D1.C, D3.C, GND.TP, GND24.TP, JP2.1 (2), JP3.1, JP5.1, Q3.2 (S), R5.1, R11.1, R12.1, R17.2, S1.1 (GND), U1.1 (/OE), U1.3 (GND), U2.1 (CTG), U2.4 (GND), U2.EP (GND), U3.5 (GND), U3.10 (GND), U3.12 (GND), U4.1 (GND), U4.5 (SDO/ADR), U4.7 (GND), U5.P$2 (2), U$1.2 (GND), U$1.21 (GND)
INT1: U3.11 (INT1), U$1.5 (WKP)
INT2: U3.9 (INT2), U$1.4 (RX)
IRQ: IRQ.TP, U$1.18 (D5)
unnamed: Q1.1 (G), R7.2, R10.1
unnamed: F1.1, JP2.2 (1)
unnamed: Q3.3 (D), R10.2
unnamed: JP5.2, Q2.3 (D)
unnamed: R9.1, U$1.6 (DAC)
unnamed: +VE.TP, Q1.3 (D)
unnamed: R8.1, U$1.17 (D4)
unnamed: R6.1, U$1.8 (A4)
unnamed: D1.A, R13.2
unnamed: R13.1, U$1.7 (A5)
unnamed: R15.2, VBATT.TP
unnamed: KEEP_AWAKE.TP, R17.1, U$1.10 (A2)
unnamed: D3.A, R6.2
unnamed: DIN.TP, R1.2
unnamed: R15.1, U2.2 (CELL)
unnamed: R1.1, U1.4 (Y)
unnamed: D+.TP, U$1.31 (USB_D+)
unnamed: C3.1, U3.2 (BYP)
unnamed: D-.TP, U$1.30 (USB_D-)
NEOPIXELS: U1.2 (A), U$1.19 (D6)
NEOPIXEL_POWER: Q3.1 (G), R9.2, R12.2
NFC_POWER: Q2.1 (G), R8.2, R11.2, R16.1
RST: RST.TP, U$1.20 (D7)
SCALE_CLOCK: JP3.2, U$1.16 (D3)
SCALE_DATA: JP3.3, U$1.15 (D2)
SCL: JP5.4, R4.1, U2.7 (SCL), U3.4 (SCL), U4.4 (SCK/SCL), U$1.14 (D1)
SDA: JP5.3, R3.1, U2.8 (SDA), U3.6 (SDA), U4.3 (SDI/SDA), U$1.13 (D0)
SETUP: SETUP.TP, U$1.26 (!SETUP)
VBAT: U$1.22 (VBAT)
VIN: C1.A (+), F1.2, Q1.2 (S), R2.2, R7.1, U1.5 (VCC), U$1.1 (VIN)
VIN_MONITOR: R2.1, R5.2, U$1.11 (A1)

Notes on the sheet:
Addr: 0x1C
Acceleromiter
R11 - Probably not needed - check to see sleep state of Photon WRT enabling NFC
Optional Neopixesl
NFC Reader
Optional Acceleromiter
Temperature
Scale
Power
Optional: Battery Monitor
Optional: T/RH/BP
Tap sense to allow the scale to wake up when a bottle is place on it.
Buzzer to notify the user the weight has been measured
KEEP_AWAKE: connect to 3v3 TP to keep Photon awake
Stephen Harrison
V1.1

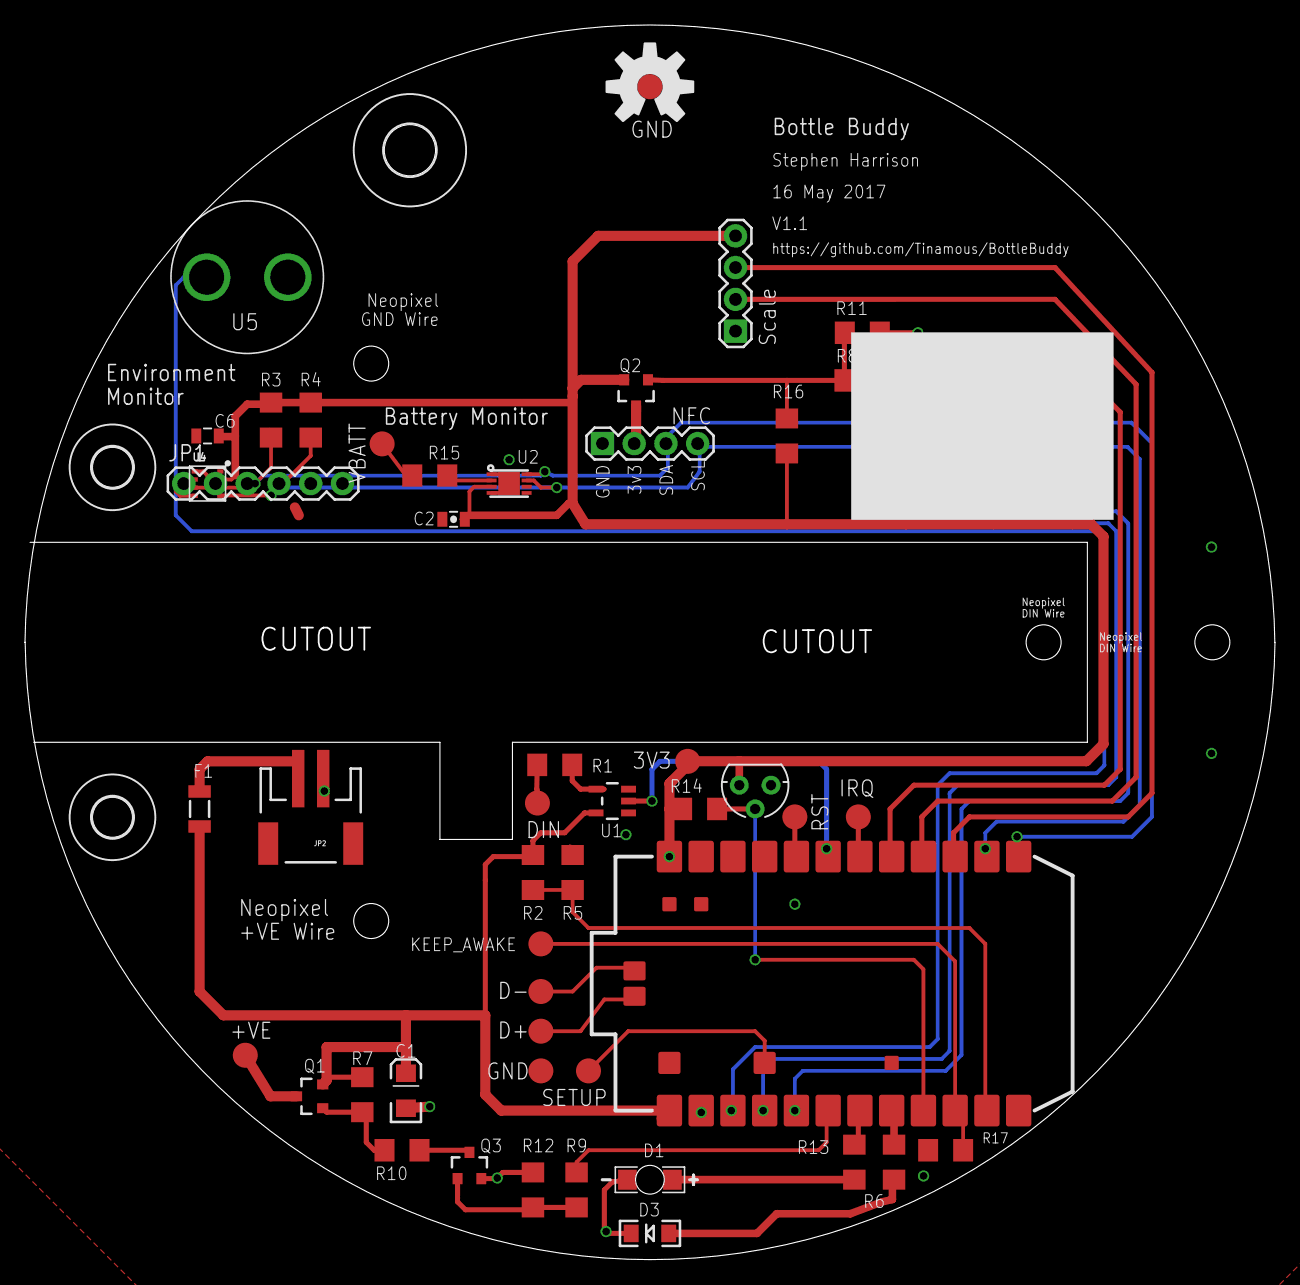
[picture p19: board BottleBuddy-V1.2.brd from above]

Board: 2 copper layers, 100.0 x 98.8 mm, 59 parts (1 on the bottom side), 37 nets.

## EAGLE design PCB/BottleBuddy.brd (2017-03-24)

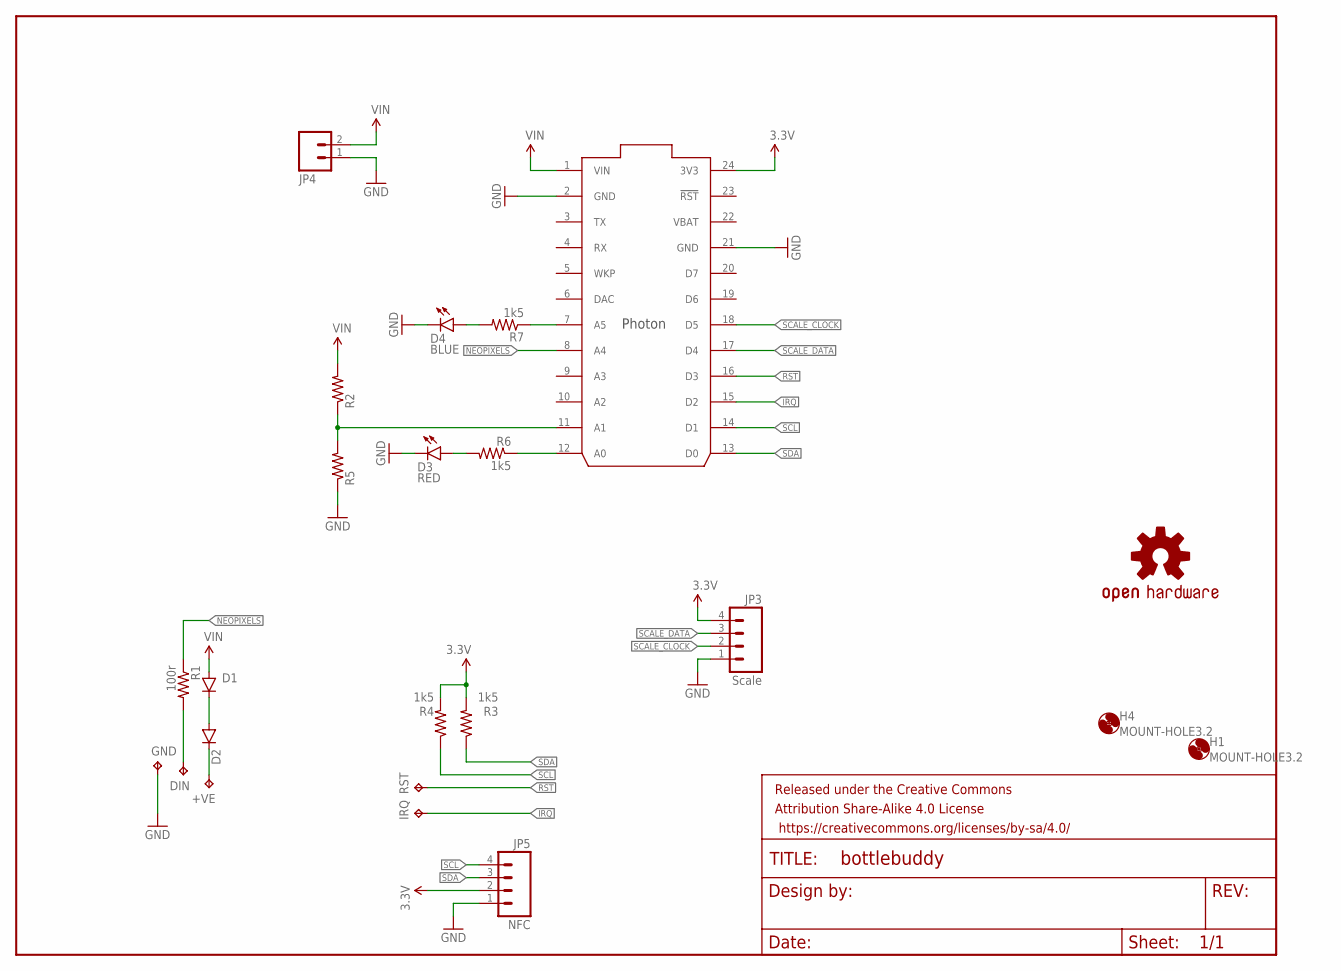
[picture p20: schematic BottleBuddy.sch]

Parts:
+VE: TPTP20R; TP20R
D1, D2: DIODESMA; SMA-DIODE
D3: RED; LED-1206
D4: BLUE; LED-1206
DIN: TPTP20R; TP20R
FRAME1: FRAME-LETTER; CREATIVE_COMMONS
GND: TPTP20R; TP20R
H1, H4: MOUNT-HOLE3.2; 3,2
IRQ: NFC IRQ; TP20R
JP3: Scale; 1X04
JP4: M02-JST-2MM-SMT; JST-2-SMD
JP5: NFC; 1X04
LOGO2: OSHW-LOGOL; OSHW-LOGO-L
R1: 100r; 1206
R2, R5: RESISTOR1206; 1206
R3, R4, R6, R7: 1k5; 1206
RST: TPTP20R; TP20R
U$1: PHOTON_WITH_HEADERS; PHOTON

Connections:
3.3V: JP3.4, JP5.2, R3.2, R4.2, U$1.24 (3V3)
GND: D3.C, D4.C, GND.TP, JP3.1, JP4.1 (2), JP5.1, R5.1, U$1.2 (GND), U$1.21 (GND)
IRQ: IRQ.TP, U$1.15 (D2)
unnamed: R7.1, U$1.7 (A5)
unnamed: R2.1, R5.2, U$1.11 (A1)
unnamed: D4.A, R7.2
unnamed: D1.C, D2.A
unnamed: +VE.TP, D2.C
unnamed: R6.1, U$1.12 (A0)
unnamed: D3.A, R6.2
unnamed: DIN.TP, R1.2
NEOPIXELS: R1.1, U$1.8 (A4)
RST: RST.TP, U$1.16 (D3)
SCALE_CLOCK: JP3.2, U$1.18 (D5)
SCALE_DATA: JP3.3, U$1.17 (D4)
SCL: JP5.4, R4.1, U$1.14 (D1)
SDA: JP5.3, R3.1, U$1.13 (D0)
VBAT: U$1.22 (VBAT)
VIN: D1.A, JP4.2 (1), R2.2, U$1.1 (VIN)

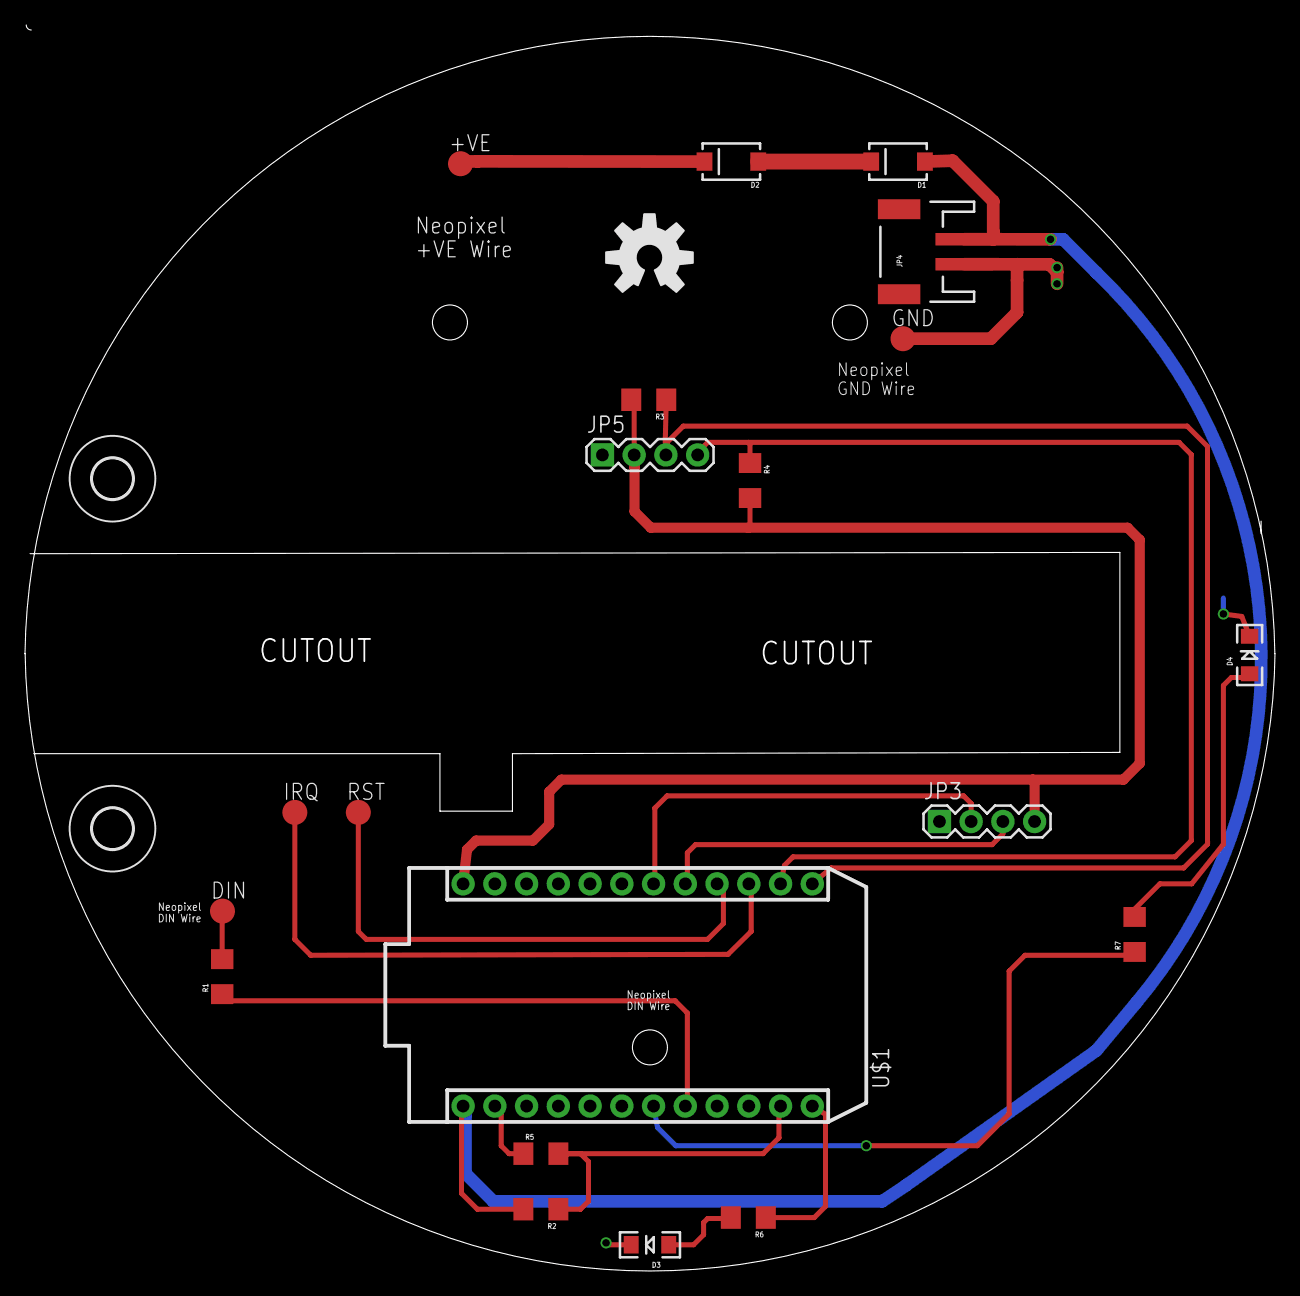
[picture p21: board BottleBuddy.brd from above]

Board: 2 copper layers, 100.0 x 99.7 mm, 24 parts (0 on the bottom side), 18 nets.

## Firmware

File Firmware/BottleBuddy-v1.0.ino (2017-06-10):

// This #include statement was automatically added by the Particle IDE.
#include <OneWire.h>
#include "DS18.h"

// This #include statement was automatically added by the Particle IDE.
#include "SparkFunMMA8452Q.h"

// This #include statement was automatically added by the Particle IDE.
#include <neopixel.h>

// This #include statement was automatically added by the Particle IDE.
#include <Adafruit_PN532.h>
// See: https://github.com/adafruit/Adafruit-PN532/blob/master/examples/iso14443a_uid/iso14443a_uid.pde

// This #include statement was automatically added by the Particle IDE.
#include "HX711.h"
// See https://github.com/bogde/HX711/blob/master/README.md

// Pin out...
//                  V1.0        V1.1
// NFC PN532 device.
// NFC I2C SDA      D0          D0
// NFC I2C SCL      D1          D1
// NFC IRQ          D2          D5
// NFC RSTO         D3          D7
// NFC RSTPDN       D6          D4  

// HX711 Load Cell
// HX711 Data       D4          D2
// HX711 CLK        D5          D3

// Additional
// VIN Sensor       A1          A1
// Red LED          A0          
// Blue LED         A5          
// Reverse LED                  A5

// NeoPixels        -- (was A4) D6
// Buzzer           A4          A4
// Accel IRQ        WKP         WKP

// NeoPizel Power               DAC
// DS18B20 DQ       A3          A3
// Keep Awake       A2          A2

String applicationVersion = "0.34";

// Run WiFi network stuff on a seperate thread.
SYSTEM_THREAD(ENABLED);

// Don't connect unless we need to.
SYSTEM_MODE(SEMI_AUTOMATIC);

//STARTUP(System.enableFeature(FEATURE_RETAINED_MEMORY));

// Memory Mapping
// 
// EEPROM_VERSION_ADDRESS = 0x00;     // Version of the eeprom mapping
// Tare value for the load cell
// TARE_ADDRESS = 0x04;
// What mode we are in (spot weight, continious, ....)
// DEVICE_MODE_ADDRESS = 0x08;

// Tracked weight of the object on the scales.
double currentWeight = 0.0f;
String currentBottleId = "";

// parameter "gain" is ommited; the default value 128 is used by the library
#define SCALE_DATA_PIN D4
#define SCALE_CLOCK_PIN D5
HX711 scale(SCALE_DATA_PIN, SCALE_CLOCK_PIN);

// Raw tare for the load cell.
// Not, a zero value for empty scale (see emptyWeight)
// Should be set on an empty scale
// when powered up. 
long tareValue = 0;

// NFC Set-up
#define NFC_RESET_PIN D3
#define NFC_IRQ_PIN D2
#define NFC_RSTPDN_PIN D6
Adafruit_PN532 nfc(NFC_IRQ_PIN, NFC_RESET_PIN); // I2C Mode
//Adafruit_PN532 nfc(NFC_IRQ_PIN, NFC_RSTPDN_PIN); // I2C Mode

// NeoPixel Setup
//#define PIXEL_PIN A4
//#define PIXEL_COUNT 24
//#define PIXEL_TYPE WS2812B

//Adafruit_NeoPixel strip(PIXEL_COUNT, PIXEL_PIN, PIXEL_TYPE);

// ================================
// Acceleromiter for tap detection
// Create an MMA8452Q object
// Default constructor, SA0 pin is HIGH (addr: 0x1D)
// eBay board has SA0 1k to GND addr: 0x1C
// pulling high = 3mA current consumption baseline.
MMA8452Q accel(MMA8452Q_ADD_SA0_0); 

// ================================
// Environmental
// BME280....
bool hasEnvironmentalSensor = true;
double temperature = 0;
double humidity = 0;
double pressure = 0;

// Temperature from the DS18B20
bool hasValidTemperature = false;
double oneWireTemperature = 0;

DS18 sensor(A3);

// ================================
// Battery monitor
#define VIN_MONITOR_PIN A1
// VIN in terms of ADC bits.
int vin = 0;

// ================================
// LEDs
#define LED_1_PIN A5
#define LED_2_PIN A0
//int led1 = A5;
//int led2 = A0;

// ================================
bool checkBottle = false;
Timer timer(60000, timerTick);

String senml;

// ================================
// Power management
#define KEEP_AWAKE_PIN A2
unsigned long waketime = 0;
bool measuring = false;
bool firstLoop = true;

// measurement variables
double bottleWeight = 0;
double emptyWeight = 0;
// Difference between the bottle weight and the empty weight
double measuredBottleWeight = 0;
bool waitForItemToBeRemoved = false;

bool showDebug = false;

// ================================
// Buzzer
#define BUZZER_PIN A4

int volume = 128;

// Optimum frequency for the Piezo is 4.5kHz
// Farnell 2309143
// Multicomp: MCKPT-G1210-3916
int frequency = 4000;

// ================================
// retained variables
// 

// ========================================================================================
// Setup
// ========================================================================================

void setup() {
    // Reserve 1024 characters for the senml fields
    // Max is 255 for publish
    // However we may accidentally go over that
    // without realising it.
    senml.reserve(1024);
    
    // TODO: Check/Transform as needed.
    long eepromVersion = 1;
    EEPROM.put(0x00, eepromVersion);
    
    Serial.begin(38400);
    Serial.println("Bottle buddy initializing.");
    
    // Try to read the interrupt source early on
    // otherwise it gets lost.
	Wire.begin(); // Initialize I2C
    byte interruptSource = accel.readInterruptSource(); 
    
    setupGPIO();
    
    setupParticleFunctions();

    setupScale();
    
    setupNFCReader();
    
    setupNeoPixels();
    
    setupAccelerometer(interruptSource);
    
    // record the time we woke so we 
    // can force a sleep if no activity
    resetWakeTime();

    // High power mode.
    // Take measurements of the bottle on 
    // timed intervales.
    
    // When in keep awake the timer will cause
    // occasional environmnet checks that would normally
    // happen with the wake from deep sleep
	timer.start();
  
    // And we're ready to go....
    Serial.println("Bottle buddy initialized. " + applicationVersion);
}

void setupGPIO() {
    pinMode(VIN_MONITOR_PIN, INPUT); // Actually analog.
    pinMode(LED_1_PIN, OUTPUT);
    pinMode(LED_2_PIN, OUTPUT);
    pinMode(KEEP_AWAKE_PIN, INPUT_PULLDOWN);
    pinMode(BUZZER_PIN, OUTPUT);
    pinMode(NFC_RSTPDN_PIN, OUTPUT);
    
    // Debug LED (RST on V1.1 PCB so need to becareful)
    pinMode(D7, OUTPUT);
    
    digitalWrite(LED_1_PIN, HIGH);
    digitalWrite(LED_2_PIN, LOW);
}

void setupParticleFunctions() {
    Particle.function("readRfid", readRfid);
    Particle.function("readWeight", readWeight);
    Particle.function("cal", calibrate);
    Particle.function("tare", tare);
}

void setupScale() {
    // this value is obtained by calibrating the scale with known weights; see the README for details
    scale.set_scale(400.8f);
    
    // Need to tare the scales when no bottle is present.
    // This can be done manually via the Particle function
    // or we could do it on bottle removed.
    // Might not be ideal here if restarting with an object on the scales.
    //scale.tare();	
    
    long value;
    EEPROM.get(0x04, value);
    if(value == 0xFFFFFFFF) {
        // EEPROM was empty
        tareValue = 0;
        publishStatus("No tare stored in EEPROM. Please tare scales.");
    } else {
        tareValue = value;
        publishStatus("Tare: " + String(tareValue));
    }
    
    Serial.println("Tare value: " + String(tareValue));
    
    // tareValue is a EEPROM stored value and set via 
    // a particle function.
    scale.set_offset(tareValue);
}

void setupNFCReader() {
    digitalWrite(NFC_RSTPDN_PIN, HIGH);
    delay(250);
    
    // Setup the NFC Reader
	nfc.begin();
	uint32_t versiondata = nfc.getFirmwareVersion();
	Serial.println("NFC Version: " + String(versiondata));

	// Set the max number of retry attempts to read from a card
    // This prevents us from waiting forever for a card, which is
    // the default behaviour of the PN532.
    nfc.setPassiveActivationRetries(0x10);
  
    // configure board to read RFID tags
    nfc.SAMConfig();
}

void setupNeoPixels() {
    // NeoPixel initialize
    /*
    strip.begin();
    strip.show(); // Initialize all pixels to 'off'
    */
}

void setupAccelerometer(byte interruptSource) {
    	// Initialize the accelerometer with begin():
	// begin can take two parameters: full-scale range, and output data rate (ODR).
	// Full-scale range can be: SCALE_2G, SCALE_4G, or SCALE_8G (2, 4, or 8g)
	// ODR can be: ODR_800, ODR_400, ODR_200, ODR_100, ODR_50, ODR_12, ODR_6 or ODR_1
    if (accel.begin(SCALE_2G, ODR_1) == 0) {
        connectToTheCloud();
        Particle.publish("status", "Failed to initialize accel.");
    } else {
    
        setupAccelerometerTaps();
        
        // Check for bit 3 of the interrupt being set
        // to indicate we were woken by a tap
        // NB: Cached value from before begin.
        //byte interruptSource = accel.readInterruptSource(); 
        if (interruptSource && 0x08 == 0x08) {
            // Interrupt was caused by a tap.
            wakeTune();
            // Woken by a tap, so we are measuring.
            measuring = true;
        } else if (interruptSource > 0) {
            // Interrupt caused by something other than a tap
            doubleBeep();
            connectToTheCloud();
            Particle.publish("status", "Woken by a something other than a tap, Int: " + String(interruptSource));
        } else {
            // Woken by timer, don't notify..
            // TODO: Block the sleep tune as well.
            //doubleBeep();
        }
    }
}

void setupAccelerometerTaps() {
    //byte xThs, byte yThs, byte zThs, byte timeLimit = 0xFF, byte latency = 0xFF, byte window = 0xFF
    // zThs - Z Threshold can be tuned to increase or decrease sensitivity
    // to the bottle being placed on the scale.
    accel.setupTap(0xFF, 0xFF, 0x04, 0x50, 0x20, 0x78);
    configureInterrupts();
}

void configureInterrupts() {
    // Configure the WKP to be in a pull down state
    // this pin is used by the system to wake the 
    // Photon from deep sleep mode on a rising edge.
    pinMode(WKP, INPUT_PULLDOWN);
    
    accel.enableTapInterrupts();
}

// ========================================================================================
// Loop
// ========================================================================================

void timerTick() {
    // on the next pass through the loop
    // check the bottle.
    checkBottle = true;
}
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

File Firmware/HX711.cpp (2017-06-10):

#include "application.h"
#include <HX711.h>

HX711::HX711(byte dout, byte pd_sck, byte gain) {
	begin(dout, pd_sck, gain);
}

HX711::HX711() {
}

HX711::~HX711() {
}

void HX711::begin(byte dout, byte pd_sck, byte gain) {
	PD_SCK = pd_sck;
	DOUT = dout;

	pinMode(PD_SCK, OUTPUT);
	pinMode(DOUT, INPUT);

	set_gain(gain);
}

bool HX711::is_ready() {
	return digitalRead(DOUT) == LOW;
}

void HX711::set_gain(byte gain) {
	switch (gain) {
		case 128:		// channel A, gain factor 128
			GAIN = 1;
			break;
		case 64:		// channel A, gain factor 64
			GAIN = 3;
			break;
		case 32:		// channel B, gain factor 32
			GAIN = 2;
			break;
	}

	digitalWrite(PD_SCK, LOW);
	read();
}

long HX711::read() {
	// wait for the chip to become ready
	while (!is_ready());

	unsigned long value = 0;
	uint8_t data[3] = { 0 };
	uint8_t filler = 0x00;

	// pulse the clock pin 24 times to read the data
	data[2] = shiftIn(DOUT, PD_SCK, MSBFIRST);
	data[1] = shiftIn(DOUT, PD_SCK, MSBFIRST);
	data[0] = shiftIn(DOUT, PD_SCK, MSBFIRST);

	// set the channel and the gain factor for the next reading using the clock pin
	for (unsigned int i = 0; i < GAIN; i++) {
		digitalWrite(PD_SCK, HIGH);
		digitalWrite(PD_SCK, LOW);
	}

	// Replicate the most significant bit to pad out a 32-bit signed integer
	if (data[2] & 0x80) {
		filler = 0xFF;
	} else {
		filler = 0x00;
	}

	// Construct a 32-bit signed integer
	value = ( static_cast<unsigned long>(filler) << 24
			| static_cast<unsigned long>(data[2]) << 16
			| static_cast<unsigned long>(data[1]) << 8
			| static_cast<unsigned long>(data[0]) );

	return static_cast<long>(value);
}

long HX711::read_average(byte times) {
	long sum = 0;
	for (byte i = 0; i < times; i++) {
		sum += read();
	}
	return sum / times;
}

double HX711::get_value(byte times) {
	return read_average(times) - OFFSET;
}

float HX711::get_units(byte times) {
	return get_value(times) / SCALE;
}

void HX711::tare(byte times) {
    // SH: changed to long (and changed sum -> average)
	long average = read_average(times);
	set_offset(average);
}

void HX711::set_scale(float scale) {
	SCALE = scale;
}

float HX711::get_scale() {
	return SCALE;
}

void HX711::set_offset(long offset) {
	OFFSET = offset;
}

long HX711::get_offset() {
	return OFFSET;
}

void HX711::power_down() {
	digitalWrite(PD_SCK, LOW);
	digitalWrite(PD_SCK, HIGH);
}

void HX711::power_up() {
	digitalWrite(PD_SCK, LOW);
}

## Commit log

2016-10-09 Moving strain gauge body to the base unit and trimming down the bottle holder.
    [BottleBank.scad, BottleBank.stl, BottleBankBase.scad, BottleBankBase.stl]
2016-10-10 Increased wall thickness to 3 as it was a little fragile.
    Changed NFC PCB to FRID-RC522 which fits completly under the bottle.
    Chnaged so top part does not encapsulate the load cell, but it is in free air in the lower body.
    [BottleBank.scad, BottleBank.stl, BottleBankBase.scad, BottleBankBase.stl]
2016-10-11 Rotated load cell.
    About to widen back "pcb" box to full width.
    [BottleBank.scad, BottleBankBase.scad, BottleBankBase.stl]
2016-10-12 Added neopixel element to top.
    Corrected sizing of load cell.
    various other improvements.
    [BottleBank.scad, BottleBank.stl, BottleBankBase.scad, BottleBankBase.stl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]
2016-10-12 Changed name to Bottle Buddy.
    [BottleBuddyBase.scad, BottleBuddyBase.stl, BottleBuddyTop.scad, BottleBuddyTop.stl]
2016-10-12 Fixed incorrect filename.
    [BottleBankBase.scad]
2017-02-19 Added skirt to go around base unit to cover gap and prevent ingress of liquids.
    [BottleBuddyTop.scad, BottleBuddyTop.stl]
2017-02-22 Setup to use Photon Wide Prototype PCB and HX711 Load Cell PCB.
    [BottleBuddyBase.scad, BottleBuddyBase.stl]
2017-02-22 Decreased the depth of the top base as the PCB didn't need so much height.
    Added small hole in rear plate to allow the Photon RGB LED to be seen - this will need filling with epoxy.
    Added cutout for Photon USB whilst not using batteries.
    ** Last version using the RFID-RC522 as this does not appear to detect newer NFC tags (esp. the sticker versions needed for the bottom of the bottles).
    [BottleBuddyTop.scad, BottleBuddyTop.stl]
2017-02-22 Added LoadCellSpacer to raise up the height of the top from the spacer whilst developing.
    [LoadCellSpacer.scad, LoadCellSpacer.stl]
2017-02-22 Added cutout for round neopixels.
    Changed RFID/NFC sensor to "red" board version which reads the newer NFC tags.
    Added options for top finish. All round or sliced through to allow front access.
    [BottleBuddyTop.scad, BottleBuddyTop.stl]
2017-02-22 Test piece for NFC and neopixel cutouts.
    [NfcAndNeoPixelCutouts.scad, NfcAndNeoPixelCutouts.stl]
2017-03-07 Corrected comments for Neopixel connection to show correct polarity.
    increased size of I2C pin cutout for Main PCB -> NFC PCB.
    Added mounts for PCB.
    [BottleBuddyTop.scad, NfcAndNeoPixelCutouts.scad]
2017-03-07 First version round main PCB.
    [BottleBuddy.brd, BottleBuddy.sch]
2017-03-07 Removed old named base file.
    [BottleBankBase.scad]
2017-03-07 Updated stls
    [BottleBuddyBase.stl, BottleBuddyTop.stl]
2017-03-07 Made base and top round to match the PCB and save the aquard sticking out square bit.
    [BottleBuddyBase.scad, BottleBuddyBase.stl, BottleBuddyTop.scad, BottleBuddyTop.stl]
2017-03-24 Minot improvements. Hollowed out inside bottom to allow PCB to be recessed and reduce the amount of material used.
    Added V3 skirt option for a 10 sided "cylinder" rather than just round.
    [BottleBuddyTop-NoSkirt.stl, BottleBuddyTop-dec.stl, BottleBuddyTop-rountdskirt.stl, BottleBuddyTop.scad]
2017-03-24 Added values to components.
    [BottleBuddy.brd, BottleBuddy.sch]
2017-03-24 Removed loadcell guard.
    Minor sizing adjustments.
    [BottleBuddyBase.scad, BottleBuddyBase.stl]
2017-03-29 Increased the thickness of the skirt for V2 skirt and increased $fn for improved curves.
    [BottleBuddyTop.scad]
2017-05-16 V1.1 PCB added:
    Updates to PCB to add accelerometer for tap detection, temp with DB18B20 as a basic or T/RH/BP with BME280, battery charge state with MAX1704x.
    Changed one LED to be reverse LED to give indication through the top.
    Added mounting for scale HX711 PCB onto the PCB.
    Added Piezo buzzer for user feedback.
    [BottleBuddy-V1.1.brd, BottleBuddy-V1.1.sch]
2017-05-16 Made base shorter as most of it is hidden by the top (unless run in open mode with no skirt of the top.
    Made top skirt thicker to make it more ridgid (although it's not centered properly.
    Added hole for LED through.
    Added more PCB mountings.
    Swapped battery / load cell PCB around on base so that a induction charger can be used directly into the Photon.
    [BottleBuddyBase.scad, BottleBuddyTop.scad]
2017-05-29 Added hole for the RSTPDN wire on the NFC module to go throuhg as well as this is needed for max powerdown powersaving.
    Added recess for second (outer) screq on the loadcell from the top to make it more uniform.
    Made the inner cutout wider for the inner base so it doesn't have such a distinct lip.
    Minor tweak to positioning of holes for I2C and RST for NFC module.
    [BottleBuddyTop.scad]
2017-06-01 Adjustment to holes for the NFX board and increased the size of the hole for it to provide easier fitting.
    Modified skirt selection to allow for different skirt selections.
    Removed dead code and tidied up.
    [BottleBuddyTop.scad]
2017-06-01 Modified V1.1 to use plug-in modules for Accelerometer and BME280 to make life easier.
    Removed one LED.
    Changed keep awake, moved DB18B20 so it can be close to the load cell and possibly fixed as it's by the fixed part.
    [BottleBuddy-V1.1.brd, BottleBuddy-V1.1.sch]
2017-06-01 What was V1.1, somewhat out of date as well know....
    Uses SMD components for acceleromoeter and BMP280.
    May not be re-used, but adding as V1.2 incase...
    [BottleBuddy-V1.2.brd, BottleBuddy-V1.2.sch]
2017-06-09 Reduced wall height as most of it is hidden by the top skirt so not needed.
    Removed unused varients of top (skirt options) and added latest build of the stls.
    [BottleBuddyBase.scad, BottleBuddyTop-NoSkirt.stl, BottleBuddyTop-dec.stl, BottleBuddyTop-rountdskirt.stl]
2017-06-09 Added the "Case" (foot really) for the ThingySticks Photon/Electron PCB with mount for load cell and holder for battery.
    [PrototypeBaseWithLoadCell.scad, PrototypeBaseWithLoadCell.stl]
2017-06-09 Tidy up and make 7mm high
    [LoadCellSpacer.scad]
2017-06-09 Moved comments.
    [BottleBuddy-V1.1.sch]
2017-06-10 Added firmware for using BottleBuddy as a reagent tracker.
2017-06-10 Moved 3D Printed case parts to the Case folder.
    [BottleBuddyBase.scad, BottleBuddyTop.scad, LoadCellModel.scad, LoadCellModel.stl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]

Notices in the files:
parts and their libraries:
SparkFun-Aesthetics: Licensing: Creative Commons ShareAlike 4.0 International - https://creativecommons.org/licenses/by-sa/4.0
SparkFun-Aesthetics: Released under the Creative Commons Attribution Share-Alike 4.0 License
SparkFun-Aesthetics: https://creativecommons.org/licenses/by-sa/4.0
